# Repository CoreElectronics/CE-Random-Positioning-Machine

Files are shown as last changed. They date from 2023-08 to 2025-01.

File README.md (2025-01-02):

# Core Electronics Random Positioning Machine

Designed by [Core Electronics](https://core-electronics.com.au/) with documentation created and delivered by [Unconvengineering](unconvengineering.au)

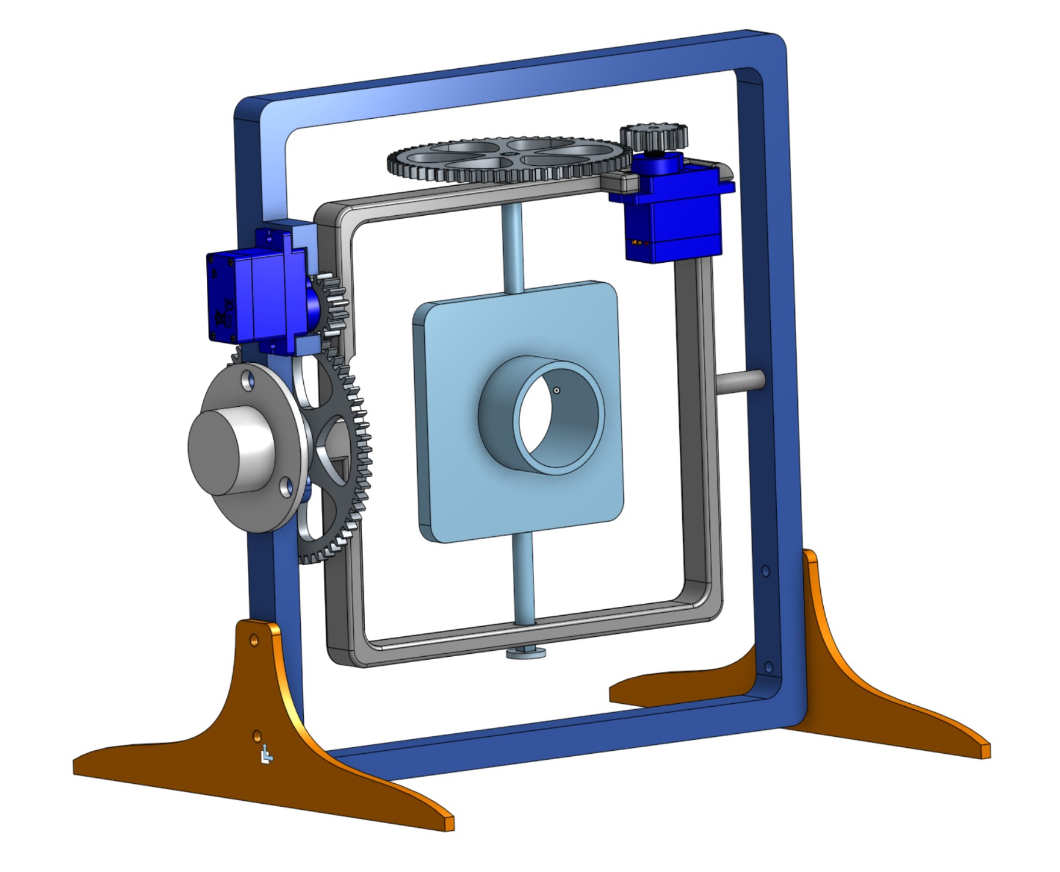
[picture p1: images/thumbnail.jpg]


## Assembly Instructions

A full bill of materials and assembly steps are covered in the instructions <a href="Assembly Instructions - Random Positioning Machine.pdf">.pdf</a>, <a href="Assembly Instructions - Random Positioning Machine.docx">.docx</a>

## Other links

- [Slip ring](https://core-electronics.com.au/slip-ring-6-wire-2a.html)
- [Micro-Servo (FS90MR)](https://core-electronics.com.au/feetech-fs90mr-1-8kg-digital-continuous-servo.html)

## OnShape Projects
This project was designed in OnShape - while all the files are available for download in this repo, we've also linked the origin project so you can
fork and modify as you see fit.

- [Gimbal Assembly](https://cad.onshape.com/documents/117125a5cf84acec012e1a52/w/c55d24c53f2760a36eea97f8/e/02a9edc0bc610c3cdac462cd?renderMode=0&uiState=64db2ebd76c08d0898801432)
- [Gear (small)](https://cad.onshape.com/documents/63b473fbdfe0cbb39b024efd/w/53a67950cdeedfac31a50e38/e/d05ef7a5c43a5f8707287d7b?renderMode=0&uiState=64db2f5d380afe075d66f8b1)
- [Gear (large, outer)](https://cad.onshape.com/documents/dbe6b9c073808e8914625170/w/710d424163e9eedf6311d957/e/28fb5d510d10226144798958?renderMode=0&uiState=64db2f33380afe075d66f8a0)
- [Gear (large, inner)](https://cad.onshape.com/documents/dbe6b9c073808e8914625170/w/710d424163e9eedf6311d957/e/28fb5d510d10226144798958?renderMode=0&uiState=64db2f33380afe075d66f8a0)

## Lab Supplies

The Random Positioning Machine is designed to be compatible with the following products. The 25mm tube is a tight fit in the experiment platform hole, or the petri dish can be adhered to the flat side of the platform.

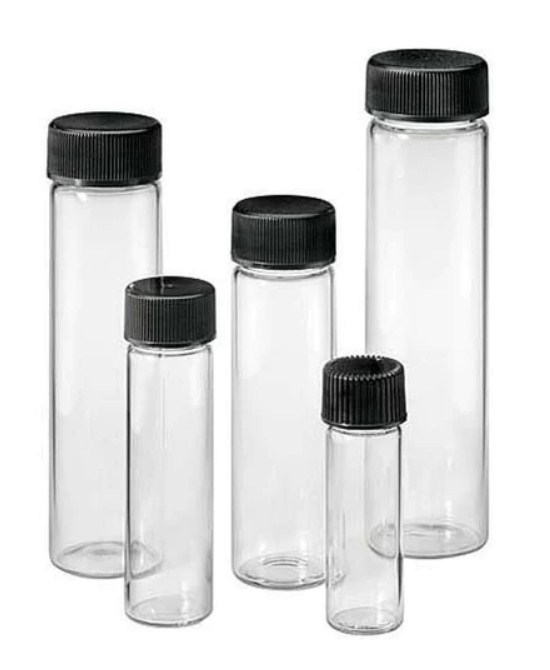
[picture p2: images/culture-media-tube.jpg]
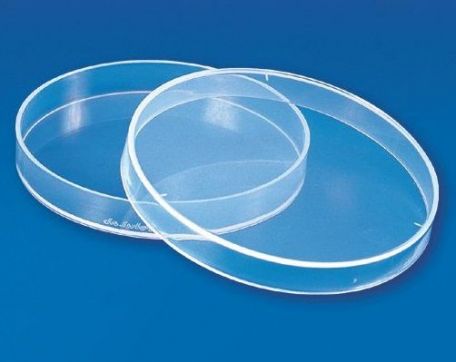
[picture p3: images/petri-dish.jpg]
 

- Culture Media Tube - 25x100mm | Science Equip SKU:[16.00.011420](https://www.scienceequip.com.au/products/culture-tubes-flat-bottom-borosilicate-clear-glass)
- 50mm Petri Dish | HAINES Educational SKU: [MAS-00622-50mm](https://www.haines.com.au/petri-dish-plastic-50mm.html)

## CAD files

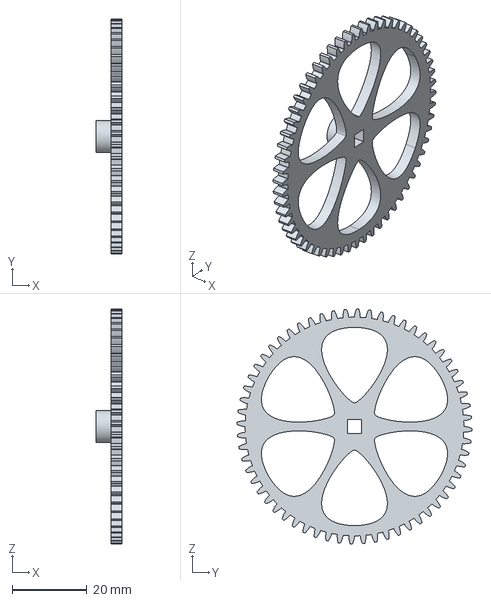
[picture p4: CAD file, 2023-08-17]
STEP/Spur Gear - Large Inner.step
7.00 x 63.0 x 63.0 mm

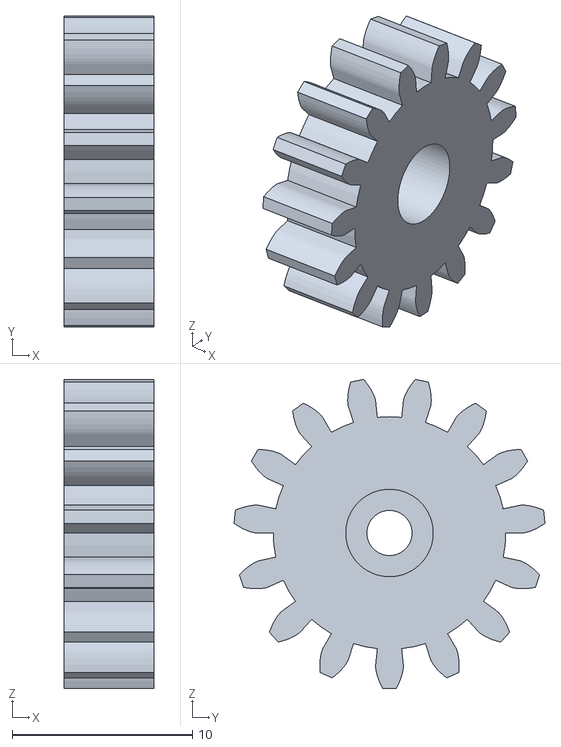
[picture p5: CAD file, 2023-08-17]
STL/Spur Gear - Small.stl
5.00 x 17.2 x 17.1

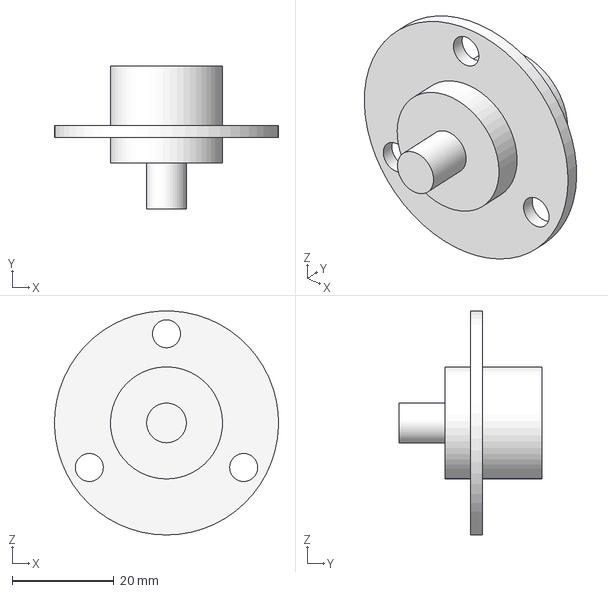
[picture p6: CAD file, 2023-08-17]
STEP/Slip ring.step
44.0 x 28.0 x 44.0 mm

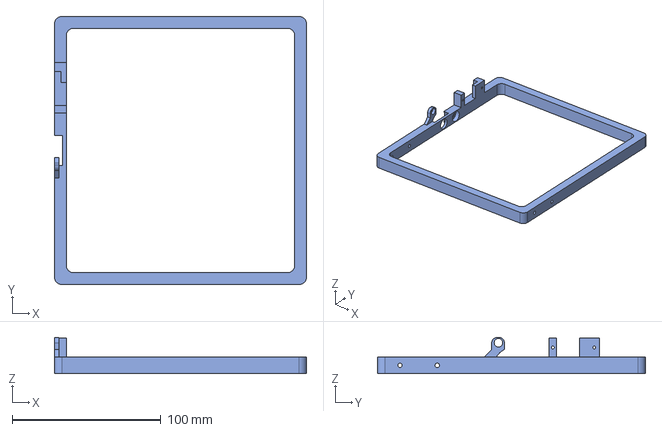
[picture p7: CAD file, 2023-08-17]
STEP/Outer Frame.step
169.2 x 179.9 x 24.2 mm

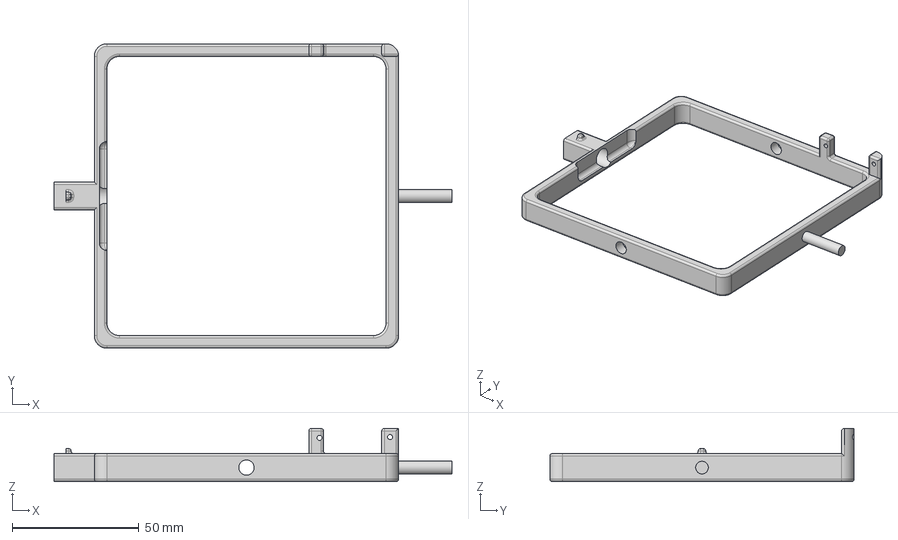
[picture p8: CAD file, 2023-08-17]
STEP/Inner Frame.step
156.9 x 120.0 x 20.9 mm

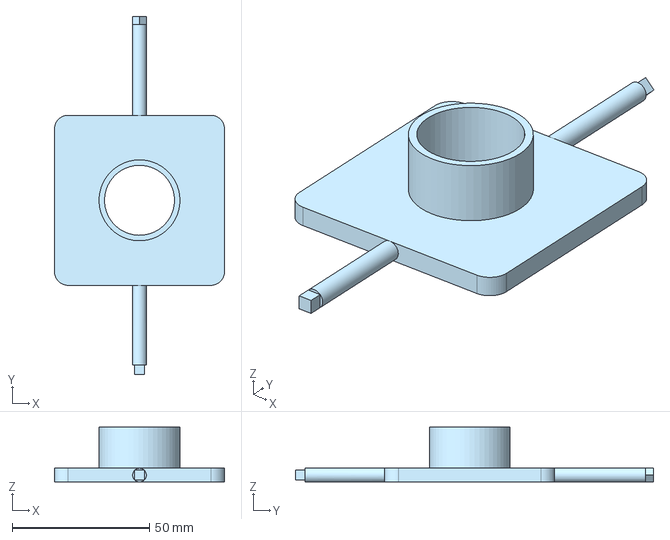
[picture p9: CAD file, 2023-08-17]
STEP/Experiment Platform.step
62.0 x 130.5 x 20.0 mm

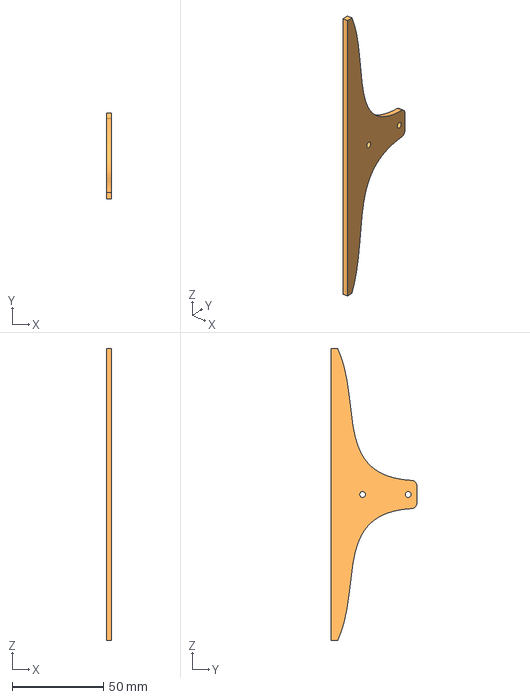
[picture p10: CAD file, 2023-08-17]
STEP/Stand.step
3.00 x 47.0 x 160.0 mm

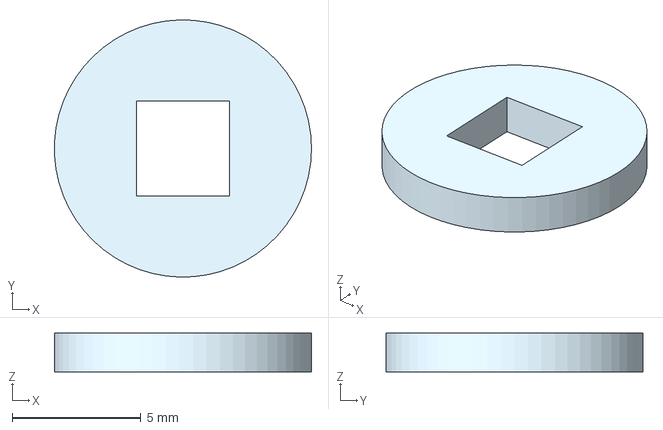
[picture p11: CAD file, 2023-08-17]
STEP/End Cap.step
9.99 x 10.00 x 1.50 mm

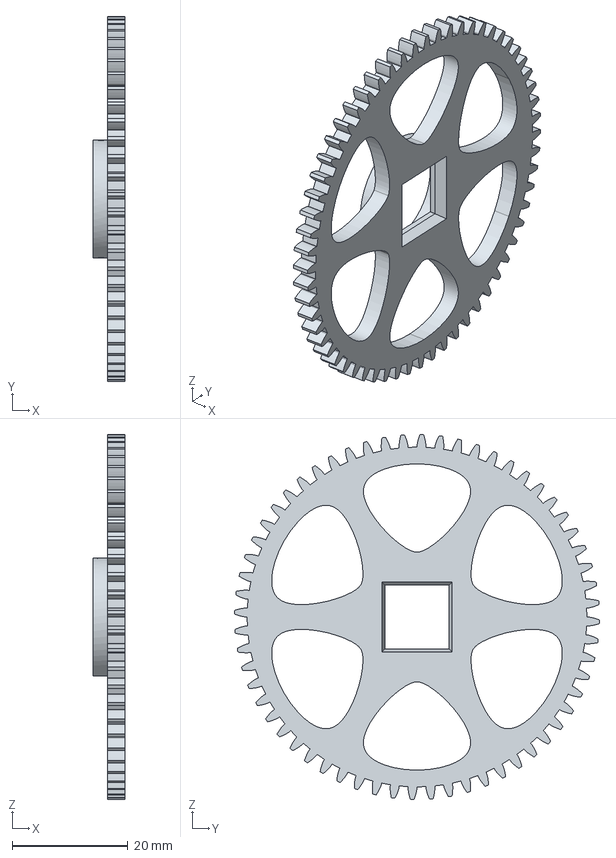
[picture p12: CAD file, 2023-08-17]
STEP/Spur Gear - Large Outer.step
5.50 x 63.0 x 63.0 mm

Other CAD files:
STL/End Cap.stl
STL/Experiment Platform.stl
STL/Inner Frame.stl
STL/Outer Frame.stl
STL/Spur Gear - Large Inner.stl
STL/Spur Gear - Large Outer.stl
STL/Stand.stl

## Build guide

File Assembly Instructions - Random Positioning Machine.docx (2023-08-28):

Random Positioning Machine Assembly Guide

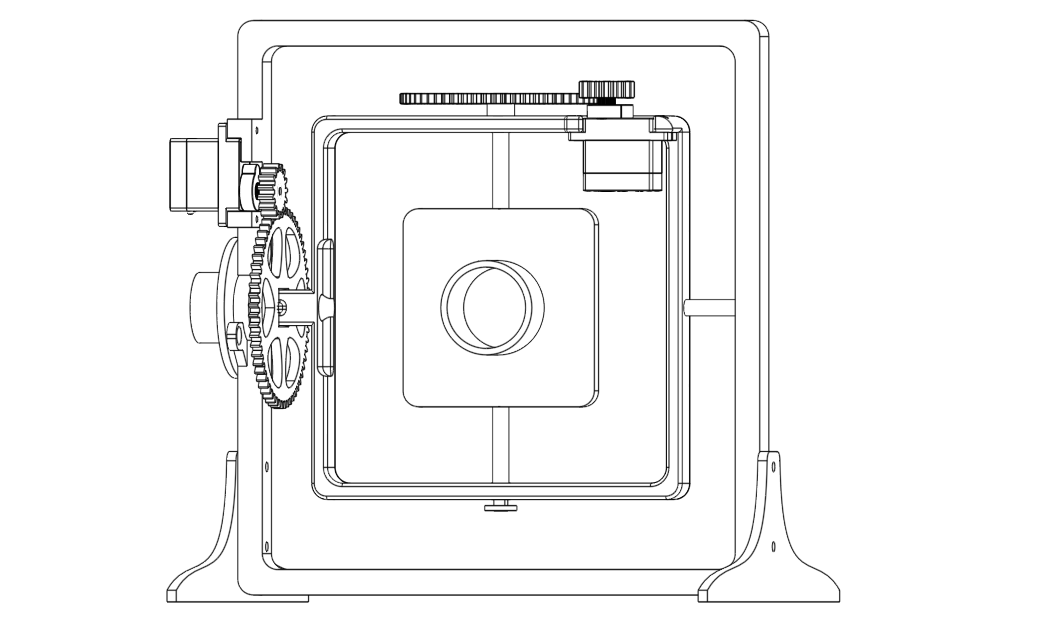
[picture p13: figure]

This project is opensource, for a copy of this guide, the code and the 3D models for printing go to https://github.com/CoreElectronics/Random-Positioning-Machine/tree/main

Preparation Work

- 3D print required parts out of PLA and clean up any edges using a file or sandpaper
- Setup MicroPython and install code on the Raspberry Pi Pico (name the code file main.py)
- Carefully attach each of the two Small Gears to a Servo and secure with a bolt
- Solder headers onto the Slip Ring wires if it does not come with headers for connection
- Source additional tools/materials needed; a screw driver, strong tape and bolt cutters for cutting off cable ties

# 1. Parts

1x Outer Frame

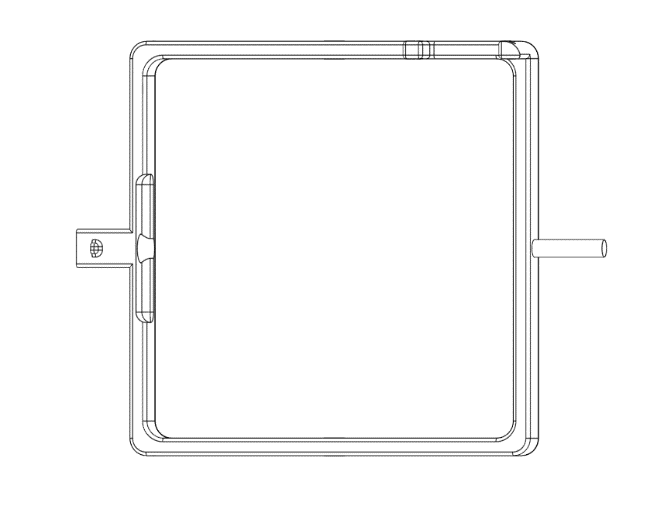
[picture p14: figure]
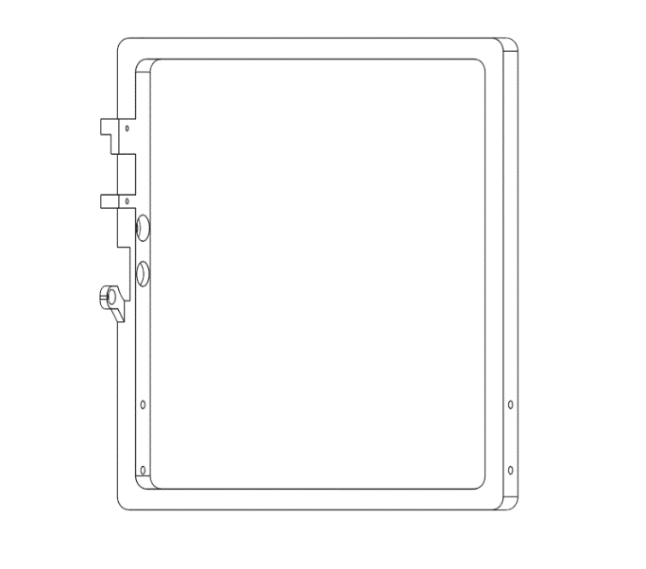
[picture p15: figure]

1x Experiment Platform

1x Inner Frame

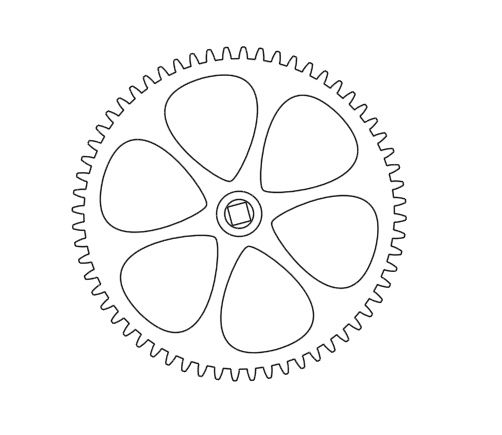
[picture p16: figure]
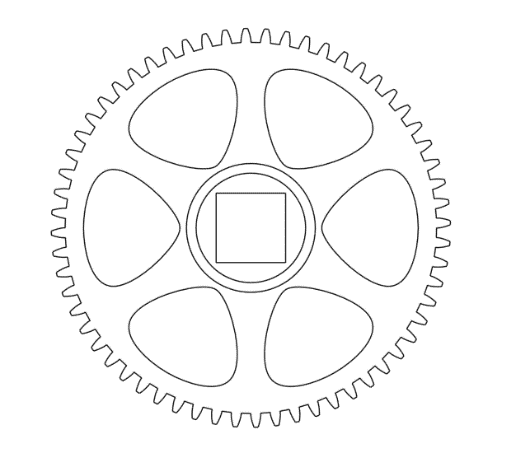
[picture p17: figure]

1x End Cap

2x Small Gear Attached to Servo

1x Inner Gear

1x Outer Gear

5x Small Cable Ties

1x Breadboard

1x Raspberry Pi Pico

4x Servo Screw

4x M3x6 Bolt

6x Jumper Wire

2x Stand

1x Long Header

1x Slip Ring

# 2. Step 1 – Inner Frame Assembly

Put the Experiment Platform through the holes on the Inner Frame, with the angled square end on the side with the raised supports.

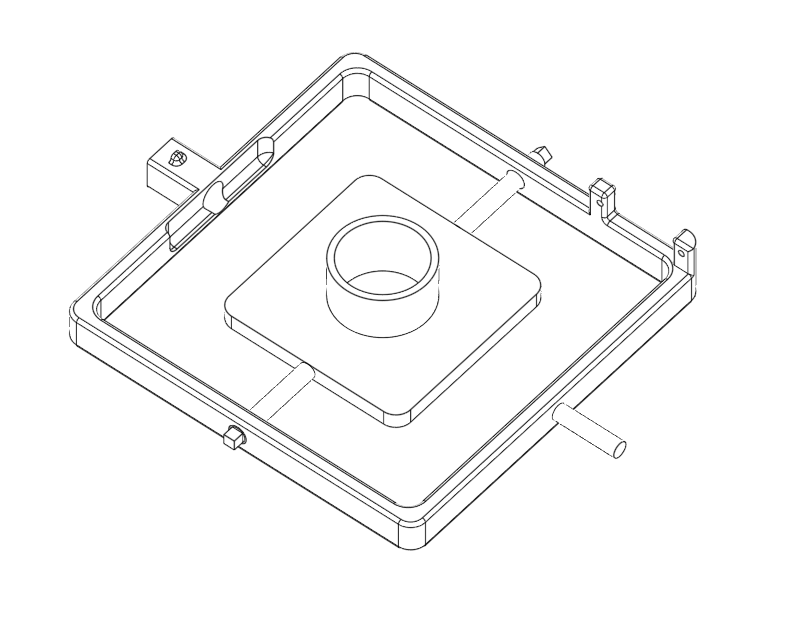
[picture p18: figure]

The Experiment Platform has two different ends, one with a straight square (below top) and one with an angled square (below bottom)

Angled Square End

Straight Square End

Put the Inner Gear on the angled square end of Experiment Platform. Make sure to put it on straight.

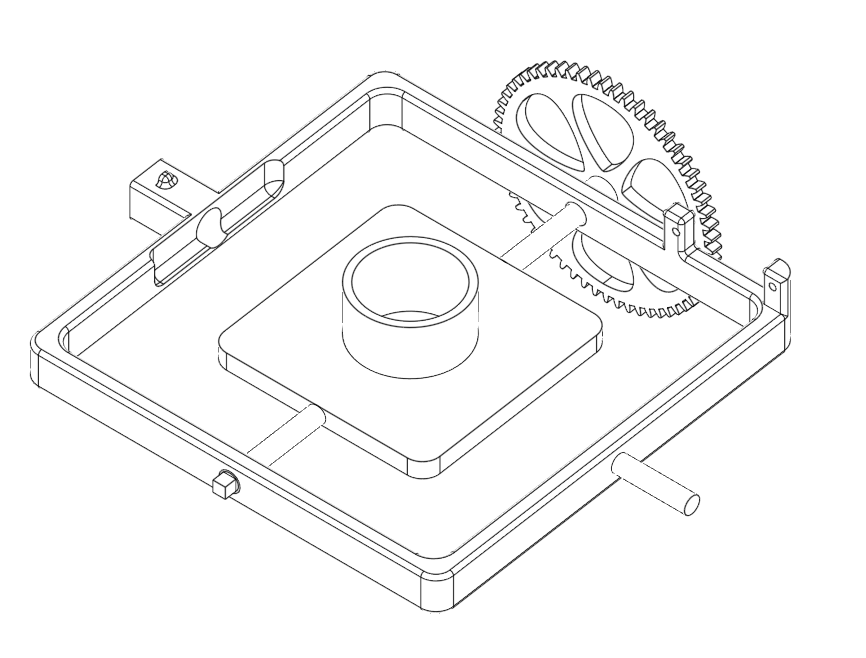
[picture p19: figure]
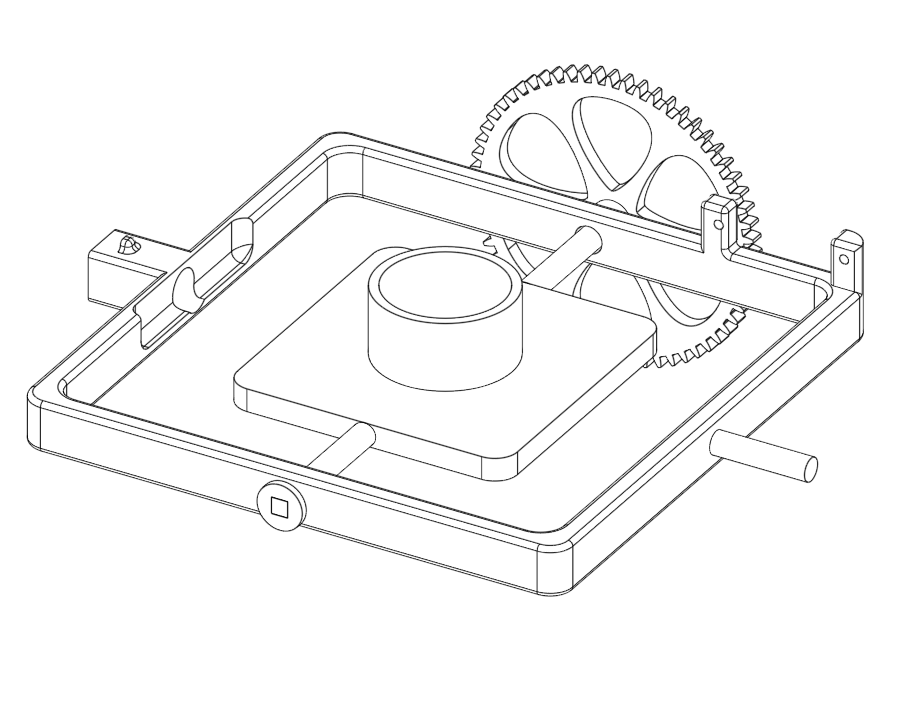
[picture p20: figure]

Put the End Cap on the straight square end of the Experiment Platform, locking the Experiment Platform in place so it does not move side to side.

# 3. Step 2 – Attach the Inner Servo

Take one of the Servos that has been preprepared with the Small Gear attached using a bolt.

Attach the Servo to the Inner Frame using two of the Servo Screws. Make sure to put the Servo in the correct position so that the Small Gear lines up with the Inner Gear.

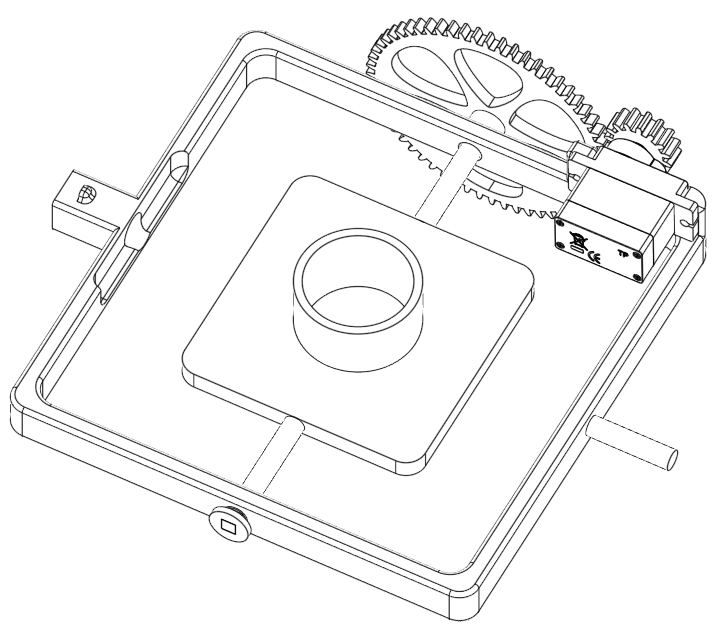
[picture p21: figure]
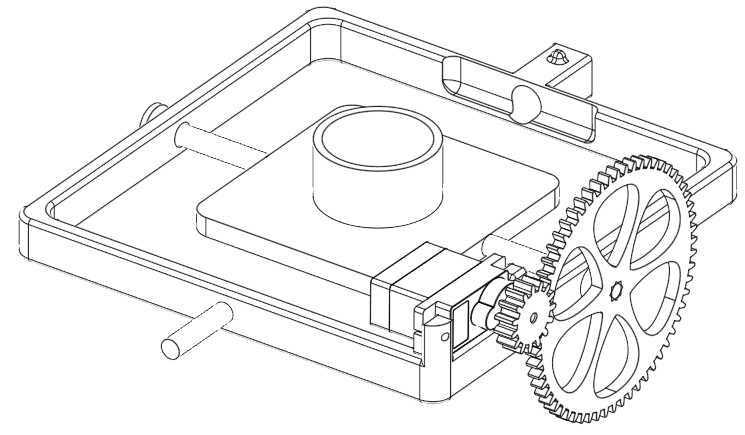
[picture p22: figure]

# 4. Step 3 – Outer Frame Assembly

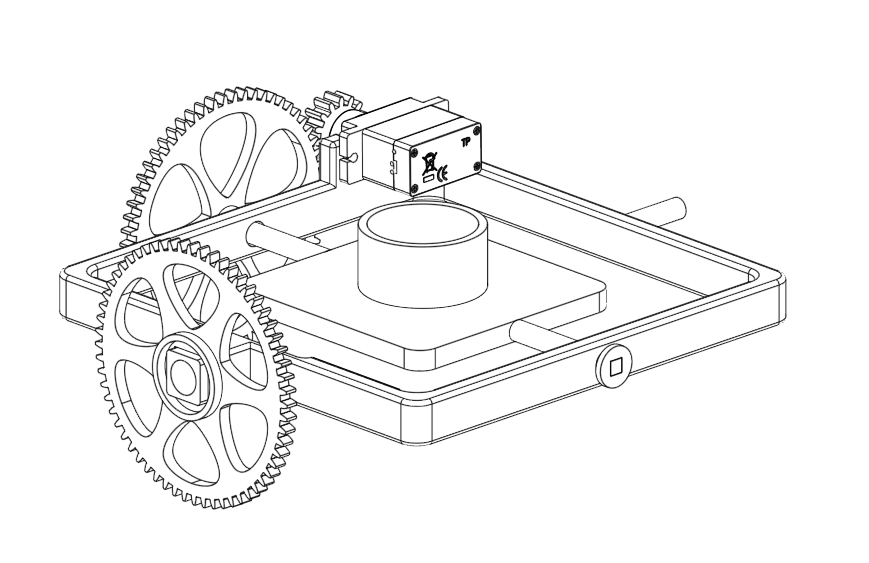
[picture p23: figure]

Put the Outer Gear on the Inner Frame. Make sure to put it on straight.

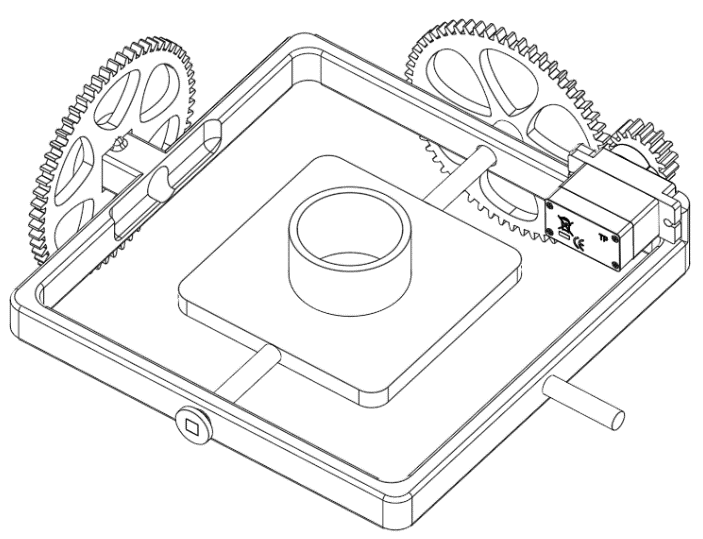
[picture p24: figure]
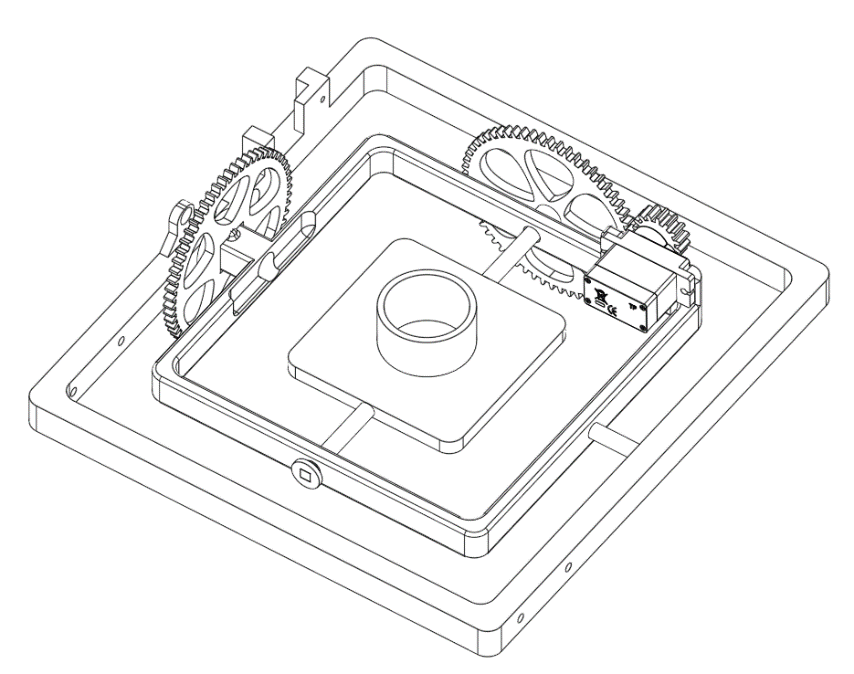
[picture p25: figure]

Put the Outer Frame on the Outer Gear.

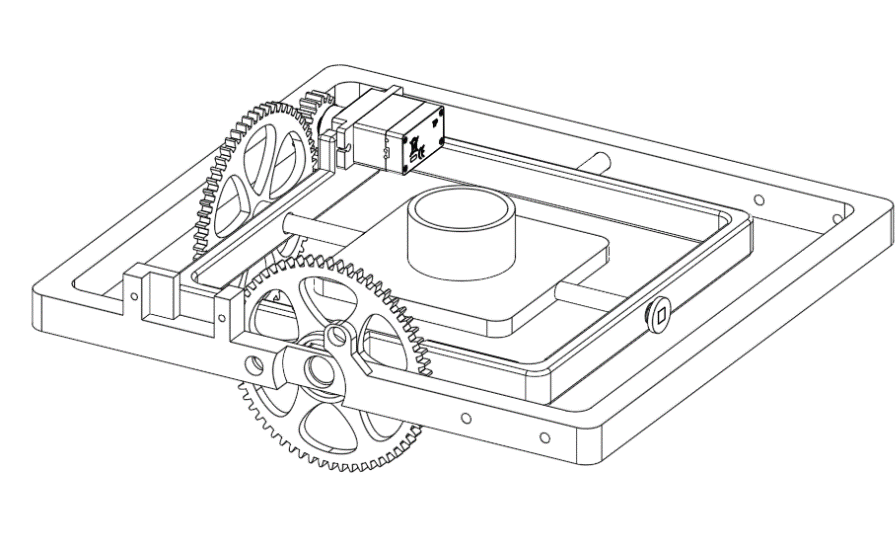
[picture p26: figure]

Put the Slip Ring through the Outer Frame into the Outer Gear, making sure to thread the Slip Ring’s shorter wire through the hole to the Inner Frame. Check the wire is not catching when the Slip Ring spins.

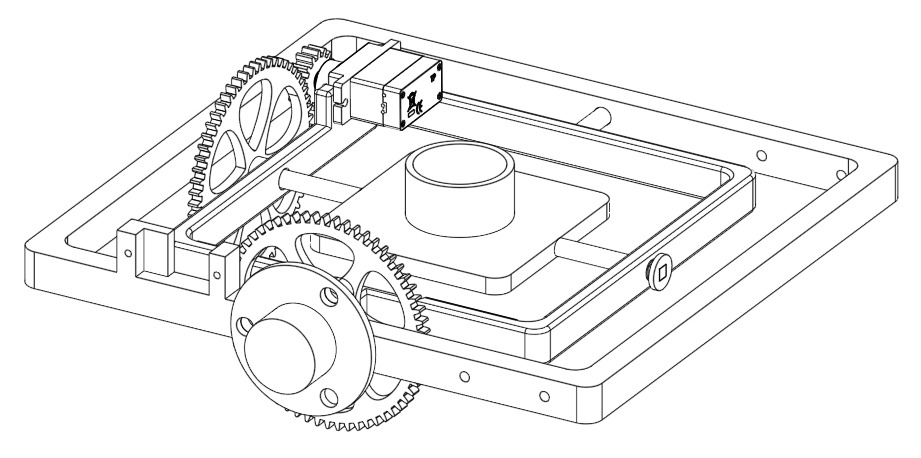
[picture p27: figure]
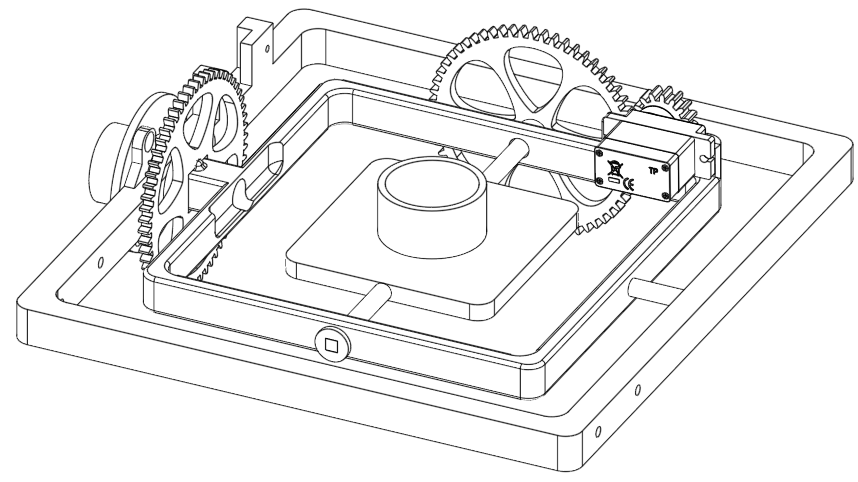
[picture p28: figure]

Secure the Slip Ring to the Outer Frame using a cable tie threaded through one of the holes on the Slip Ring and the hole on the Outer Frame as shown below.

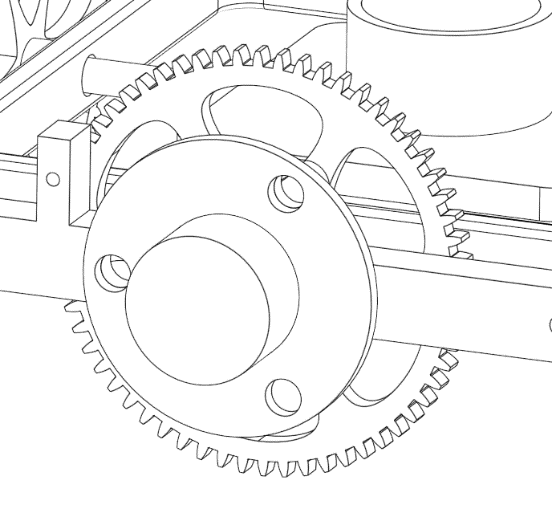
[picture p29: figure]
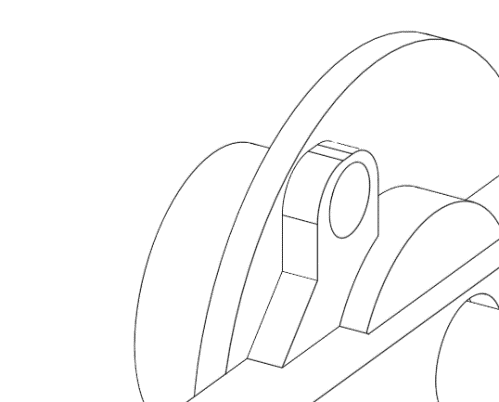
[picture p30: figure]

# 5. Step 4 – Attach the Outer Servo

Take one of the Servos that has been preprepared with the Small Gear attached using a bolt.

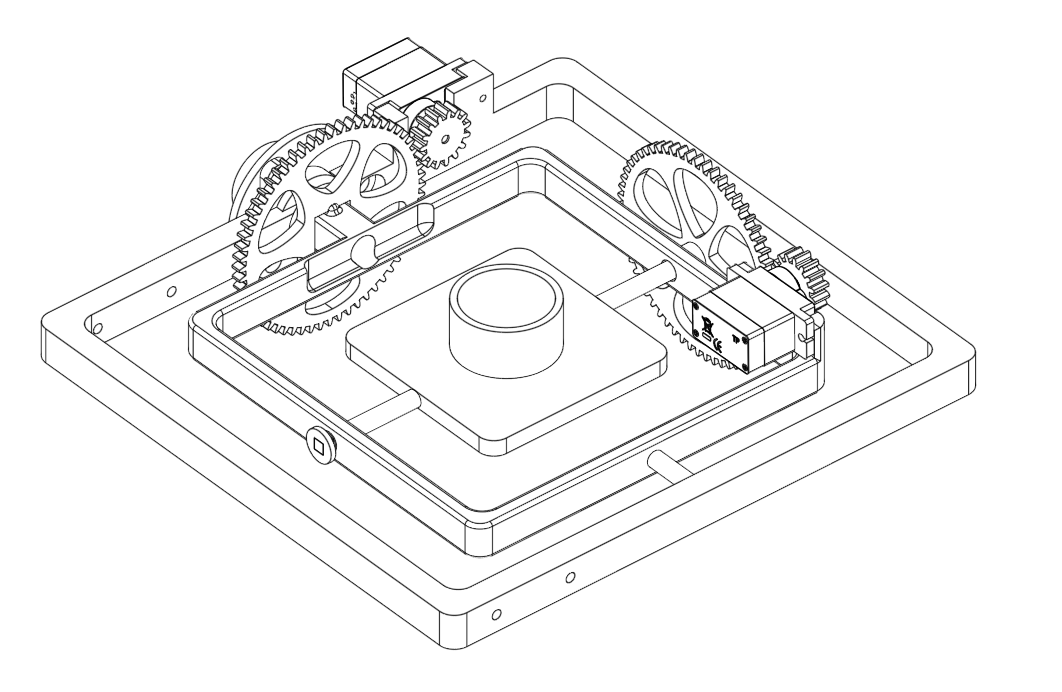
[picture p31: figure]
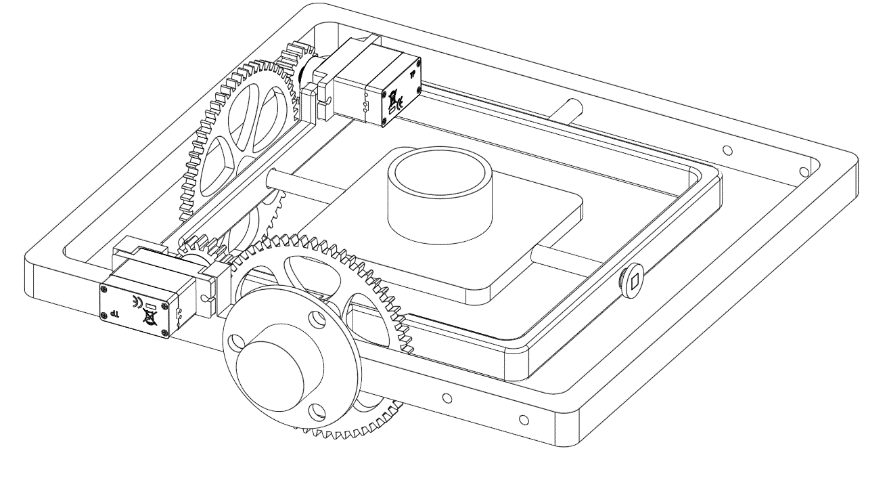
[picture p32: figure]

Attach the Servo to the Outer Frame using two of the Servo Screws. Make sure to put the Servo in the correct position so that the Small Gear lines up with the Outer Gear.

# 6. Step 5 – Attach Stands

Attach the Stands to the Outer Frame using the M3x6 Bolts.

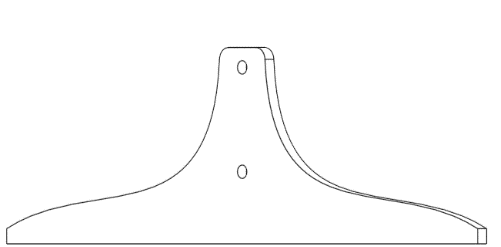
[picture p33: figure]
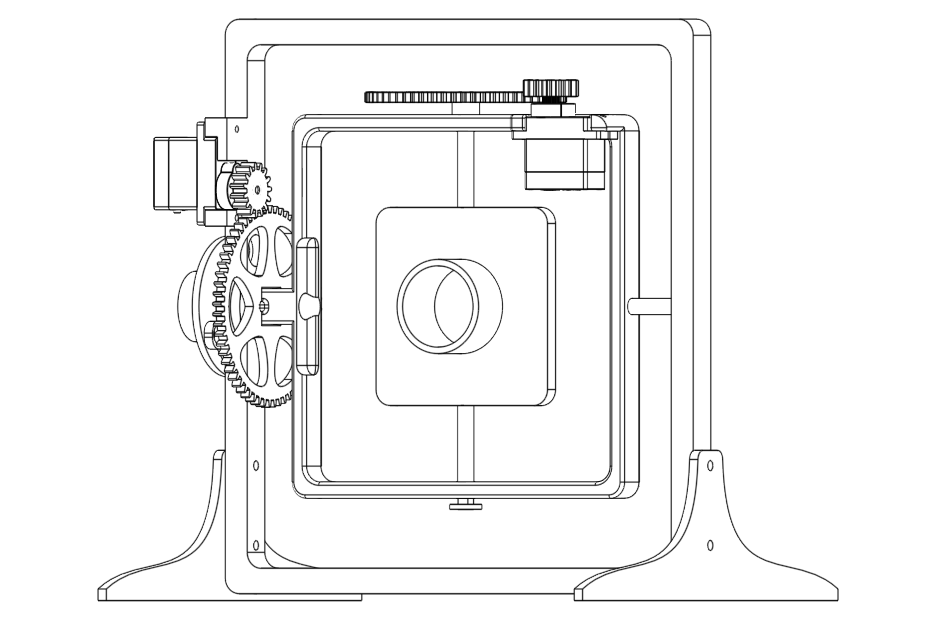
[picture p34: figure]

# 7. Step 6 – Route Cables

Connect the Inner Servo’s cable to the Slip Ring cable:

Brown -> Black

Red -> Red

Orange -> Yellow

Use tape and cable ties to attach the connected cables to the outside of the Inner Frame making sure that it will not catch on anything when the frames are spinning. If the connected cables are too long you can wrap part of them a couple of times around the Inner Frame to make it shorter when you are securing them.

# 8. Step 7 – Electronics

Place the Raspberry Pi Pico in the Breadboard with the USB end facing outward. Using the Jumper Wires connect 5 Volt power (VBUS), ground and signal pins 15 and 16 to the bottom part of the Breadboard where the cable from the Slip Ring (which is connected to the Inner Servo) and the cable from the Outer Servo will be connected to the Pico. Once everything is connected, plug the USB cable into the Pico and a power source.

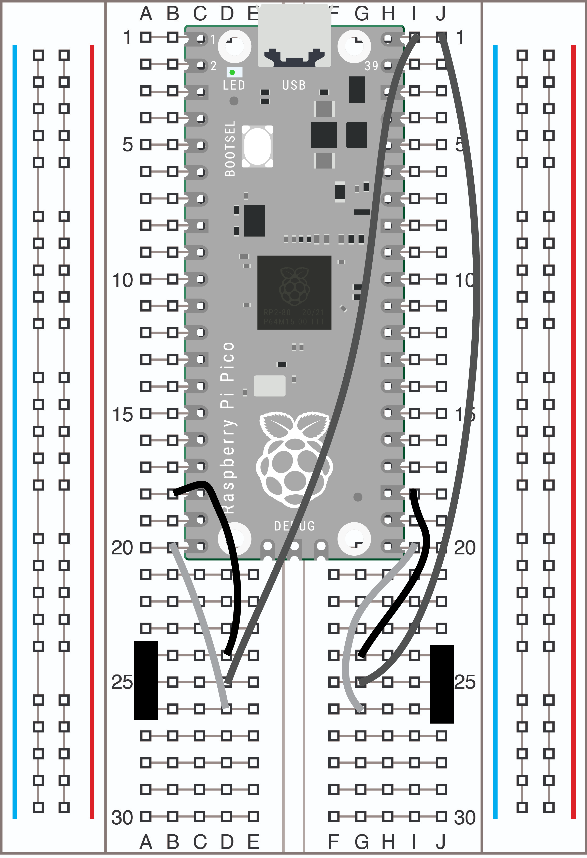
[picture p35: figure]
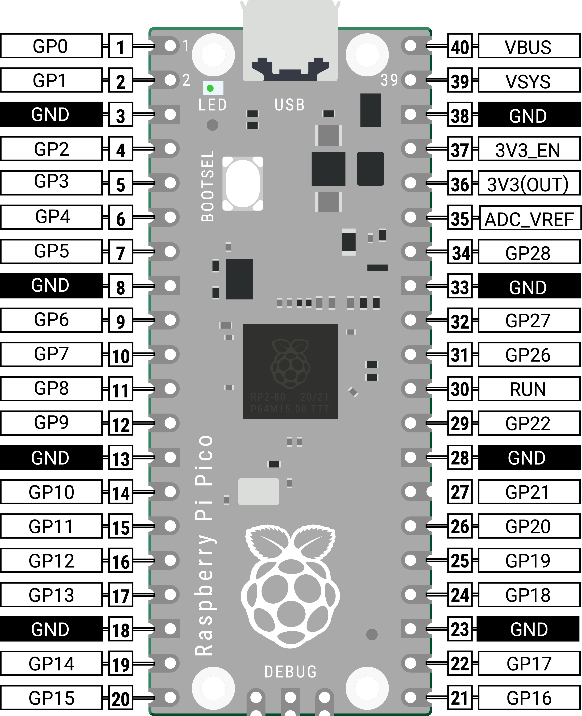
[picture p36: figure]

Cable Colours

Outer Servo Slip Ring

Brown -> Ground Black -> Ground

Red -> Power (5V) Red -> Power (5V)

Orange -> Signal GP15 Yellow -> Signal GP16

Slip Ring

Outer Servo

The Outer Servo cable is connected to the breadboard using the Long Header

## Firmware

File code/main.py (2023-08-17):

"""
Driver code the Core Electronics Random Positioning Machine
Drive the two gimbal motors with random speed setpoints that update periodically

https://github.com/CoreElectronics/CE-Random-Positioning-Machine

Runs on a Raspberry Pi Pico

Requires the micropython-servo library - https://pypi.org/project/micropython-servo/
"""

import time
from servo import Servo
import math
from random import randrange, random

# Create our Servo object, assigning the
# GPIO pin connected the PWM wire of the servo
outer_servo = Servo(pin_id=16)
inner_servo = Servo(pin_id=15)
delay_ms = 100




def modified_sine_wave(amplitude, deadband, t):
    '''removes the dead band from the centre of the sinewave. useful for driving DC motors that stall at low speeds'''
    value = amplitude * math.sin(2 * math.pi * t)
    if abs(value) < deadband:
        value = math.copysign(deadband, value) if value != 0 else deadband
    return value

frequency = 0.05 # Hz
amplitude = 25 # servos accept "speeds" between 0 and 180. most of the speed change is at low amplitudes
dead_band = 12 # dead band around where the servo changes direction. Must be smaller than amplitude

duration = 10000 # time between speed changes
last_update_time = -duration

speed_inner = setpoint_inner = 0.5
speed_outer = setpoint_outer = 0.5

try:
    while True:
        # Periodically update the speed setpoint
        if time.ticks_ms() - duration > last_update_time:
            last_update_time = time.ticks_ms()
            setpoint_inner = random()
            setpoint_outer = random()

        # Update the current speed (-1 -> 1), moving towards the setpoint smoothly 
        speed_inner = speed_inner + 0.01 * (setpoint_inner - speed_inner)
        speed_outer = speed_outer + 0.01 * (setpoint_outer - speed_outer)
        
        # Convert speed (-1 -> 1) to a servo drive signal (angle 0 -> 180), and scale down to the desired amplitude.
        drive_inner = 90 + modified_sine_wave(amplitude, dead_band, speed_inner)
        drive_outer = 90 + modified_sine_wave(amplitude, dead_band, speed_outer)
        
        # Drive the continuous servos
        inner_servo.write(drive_inner)
        outer_servo.write(drive_outer)
        
        time.sleep_ms(delay_ms)

except Exception as e:
    print(e)
finally:
    outer_servo.off()
    inner_servo.off()
